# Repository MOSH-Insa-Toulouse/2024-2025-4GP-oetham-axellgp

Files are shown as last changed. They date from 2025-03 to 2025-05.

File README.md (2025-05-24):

# 2024-2025-4GP-oetham-axellgp

## Contexte

Projet réalisé dans le cadre du cours "du capteur au banc de test", lors du deuxième semestre de l'année 2024-2025 de la formation 4ème année Génie Physique. Notre point de référence est l'article _"Pencil Drawn Strain Gauges and Chemiresistors on Paper"_ (Cheng-Wei Lin, Zhibo Zhao, Jaemyung Kim & Jiaxing Huang). Notre capteur est composé d'un simple bout de papier avec du graphite déposé dessus par un crayon à papier. Avec une simple déformation du papier, nous pouvons mesurer la déformation des particules. Le système granulaire du papier subit une modification de résistance et de conductance. Ainsi, nous pourrons utiliser ce capteur comme une jauge de contrainte traditionnelle.

L'objectif de ce projet est de pouvoir réaliser, étape par étape, un dispositif qui nous permettra de mesurer une déformation d'un capteur low-tech.

## Sommaire

- [Contexte](#contexte)
- [Sommaire](#sommaire)
- [Livrables](#livrables)
- [Matériel nécessaire](#matériel-nécessaire)
- [Simulation sur LTSpice](#simulation-sur-ltspice)
- [Design du PCB](#design-du-pcb)
- [Réalisation du Shield](#réalisation-du-shield)
- [Code Arduino](#code-arduino)
- [Application MIT](#application-mit)
- [Datasheet](#datasheet)
- [Conclusion](#conclusion)
- [Contact](#contact)

## Livrables

- Un shield PCB permettant à se relier à une carte Arduino UNO. Ce shield aura à disposition plusieurs composants : un capteur de graphite, un module bluetooth, un ecran OLED, un encodeur rotatoire et un amplificateur transimpédance avec un potentiometre digital.
- Un code Arduino qui pilotera les différents composants.
- Une application Android réalisée sous MIT App Inventor.
- Une datasheet du capteur de graphite avec les données venant d'un banc de test mis en place par les étudiants.

## Matériel nécessaire

Pour produire notre shield, nous avons besoin du matériel suivant :

- Des résistances
- Des capacités
- Un Arduino UNO
- Un amplificateur opérationnel (LTC1050)
- Un potentiomètre digital (MCP41050)
- Un écran OLED
- Un encodeur rotatoire
- Un module bluetooth (HC-05)
- Un servo moteur
- Un flex sensor

## Simulation sur LTSpice

La résistance interne de notre capteur de graphite est de l'ordre du $\text{G}\Omega$. Le courant généré lorsque nous appliquons une tension de 5V est très faible. Pour pouvoir utiliser ce signal, nous le faisons passer par un amplificateur transimpédance. Ce montage est constitué d'un amplificateur opérationnel (AO) pour fournir un signal suffisamment large au convertisseur analogique-numérique (ADC) de l'Arduino UNO.

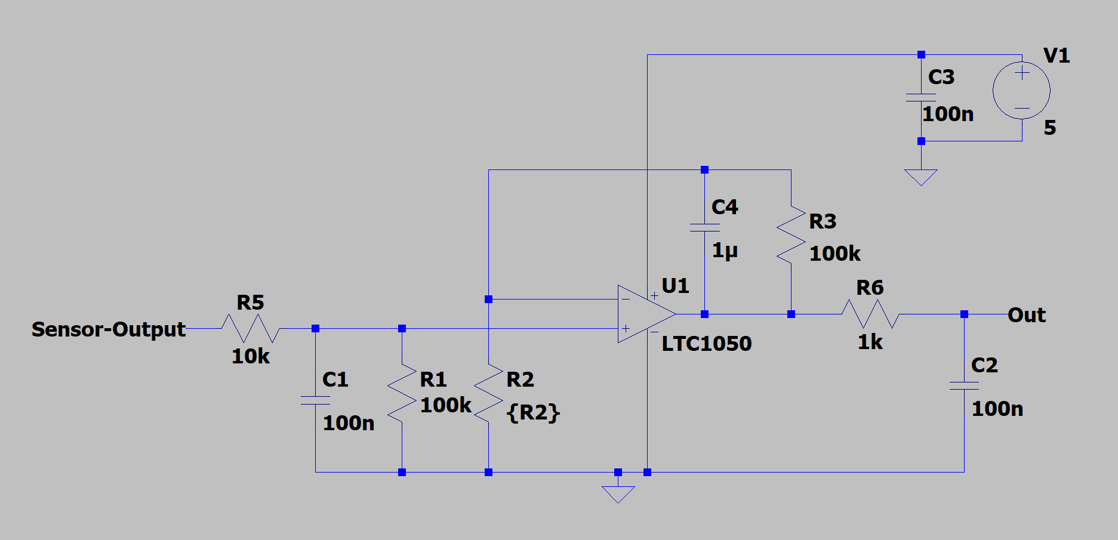
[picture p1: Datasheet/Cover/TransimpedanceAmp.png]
ltspice-circuit


Nous avons choisi un AO de type LTC1050, car il possède une capacité à accepter en entrée un courant très faible et un offset de tension bas. Nous avons besoin d'un offset faible pour ne pas fausser les valeurs de tension envoyées à l'ADC que nous aurons besoin pour la suite.

Dans notre amplificateur, nous avons trois types de filtres différents :

- À l'entrée, un filtre passe-bas passif (composants : $R_1, C_1$) avec une fréquence de coupure de 16Hz. Cela permet de filtrer les bruits du courant en entrée.
- Un autre filtre passe-bas actif de fréquence de coupure de 1.6Hz (composants : $R_3, C_4$) couplé à l'AO. Ce filtre permet d'enlever la composante du bruit à 50Hz du réseau.
- En sortie, un dernier filtre (composants : $R_6, C_2$) de 1.6kHz qui permet de retirer le bruit créé pendant le traitement i.e. bruits des alimentations, de l'horloge...

La résistance $R_5$ est placé en amont de l'AO pour le protéger contre des décharges électrostatiques. Pour notre simulation, nous avons placé la capacité $C_3$ de sorte à ce qu'elle filtre le bruit de l'alimentation. Ainsi, la résistance $R_2$ sera remplacé par une résistance variable (un potentiomètre digital) qui va nous permettre de régler le gain de notre AO en fonction de notre besoin.

Une photo pour montrer que notre montage permet à amplifier notre signal du capteur :

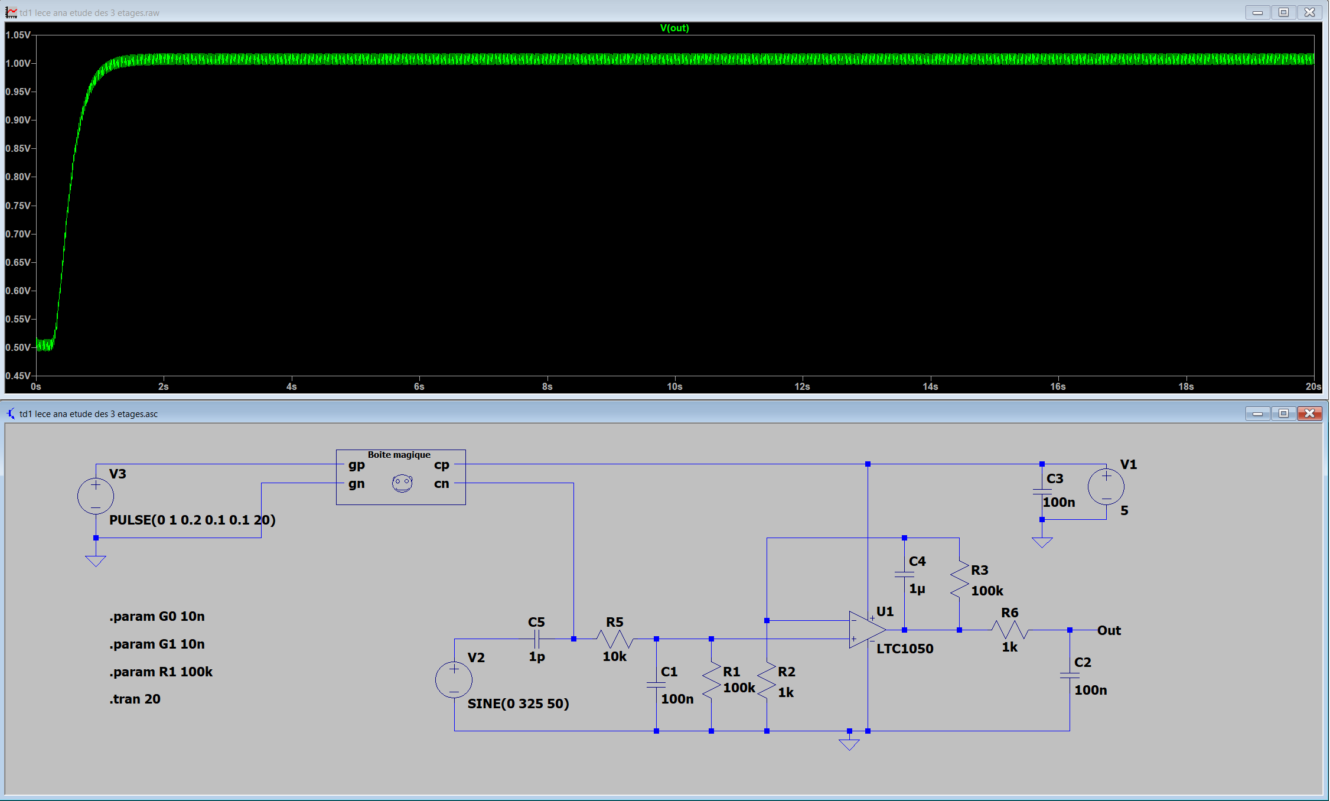
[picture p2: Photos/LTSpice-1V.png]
ltspice-amp


Le signal de sortie est amplifié à 1V, ce qui sera assez pour que notre Arduino puisse le mesurer.

Ensuite, la réponse lorsque nous simulons un courant alternatif pour vérifier que le bruit est bien filtré :

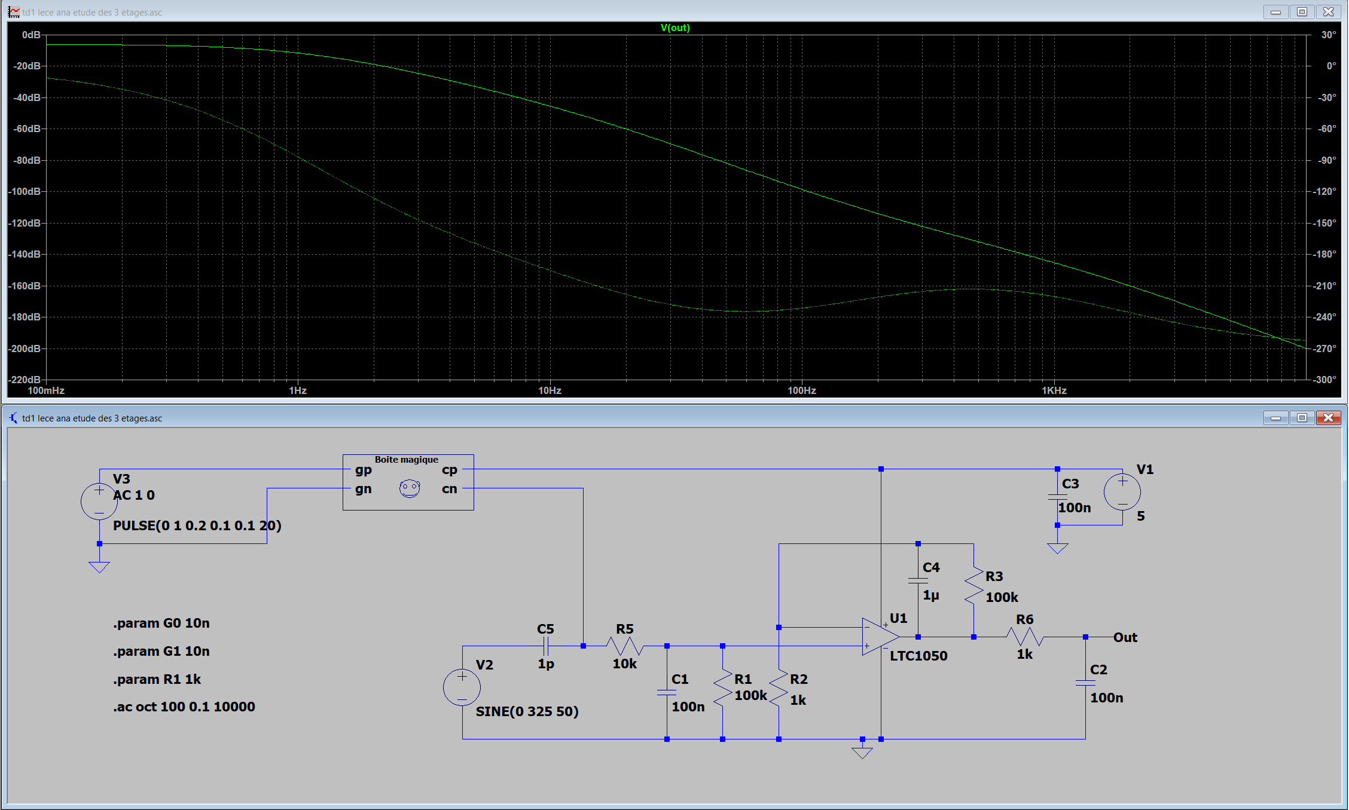
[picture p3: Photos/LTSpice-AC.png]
ltspice-ac


Le bruit du réseau est atténué d'environ 72dB.

La simulation se trouve dans [ce dossier](/LTSpice/).

## Design du PCB

Pour réaliser notre printed circuit board (PCB), nous avons utilisé le logiciel KiCAD 9.0. Dans le logiciel, nous disposons de plusieurs outils de design comme la vue schématique des composants et la vue design du PCB.

La résistance $\text{R}_2$ a été remplace par un potentiomètre numérique de manière à faire varier le gain de notre amplificateur opérationnel (LTC1050). Nous avons également rajouté des composants en plus pour mesurer plus précisément notre capteur graphite. Ces composants seront déposés sur un shield d'Arduino UNO construit à partir d'un Gerber KiCAD.

- Un flex sensor
- Un écran OLED
- Un servo moteur
- Un module bluetooth HC-05

Ensuite, nous avons commencé par réaliser les symboles des composants avec leur schéma électrique sur la partie schématique de KiCAD. Le schéma électrique de l'ensemble de notre shield :

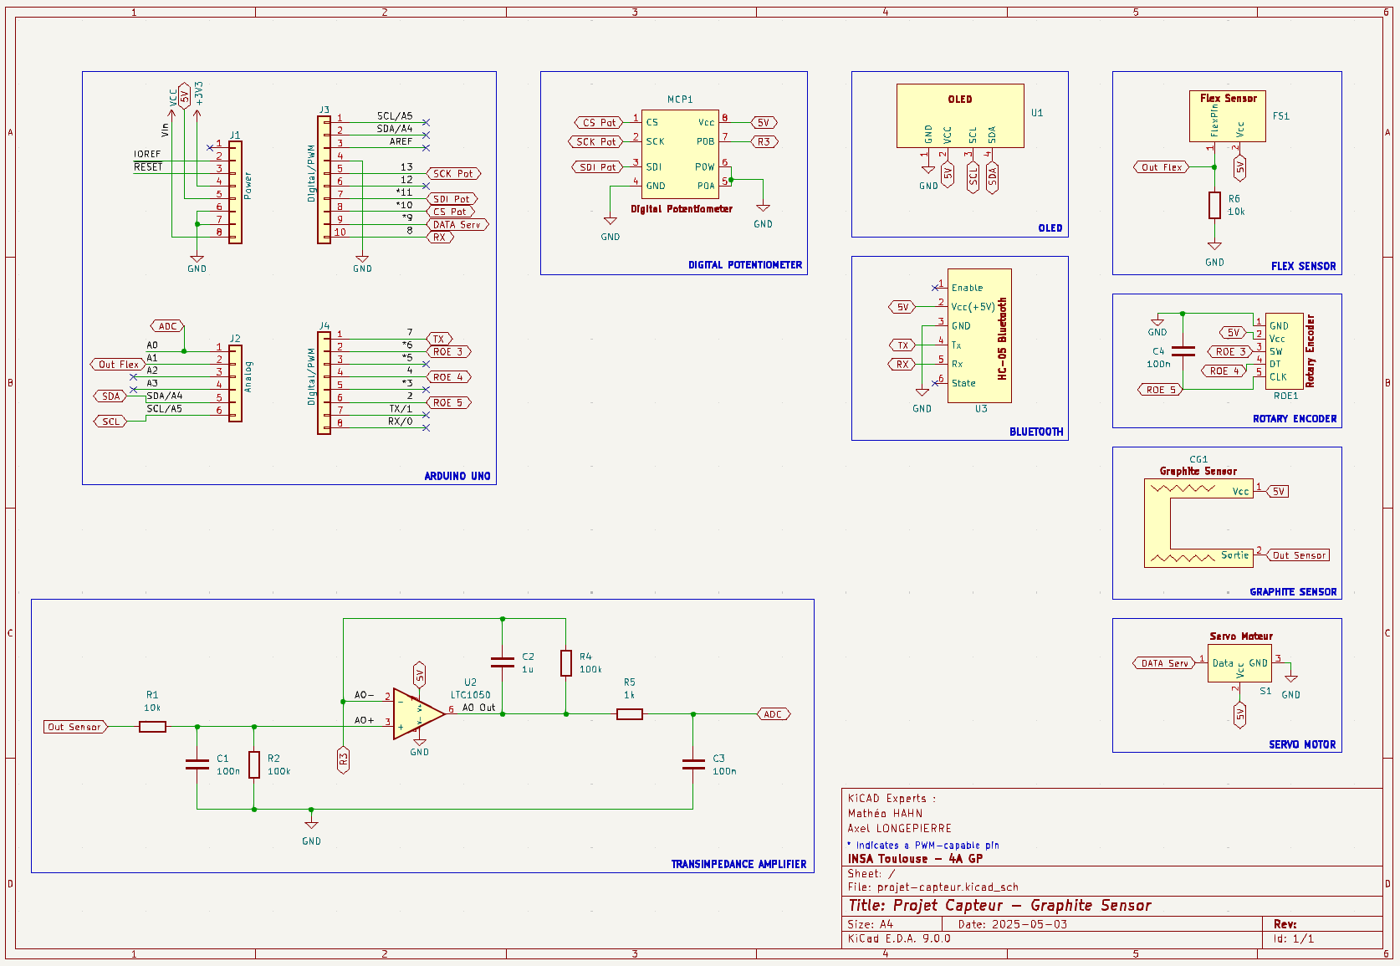
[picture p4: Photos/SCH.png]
design-sch


Par la suite, nous avons créé les empreintes de nos composants puis placées sur notre PCB sur la face PCB de KiCAD. Notre objectif pendant le routage était d'éviter les vias entraînées par le placement des composants. Le PCB créé sur le logiciel :

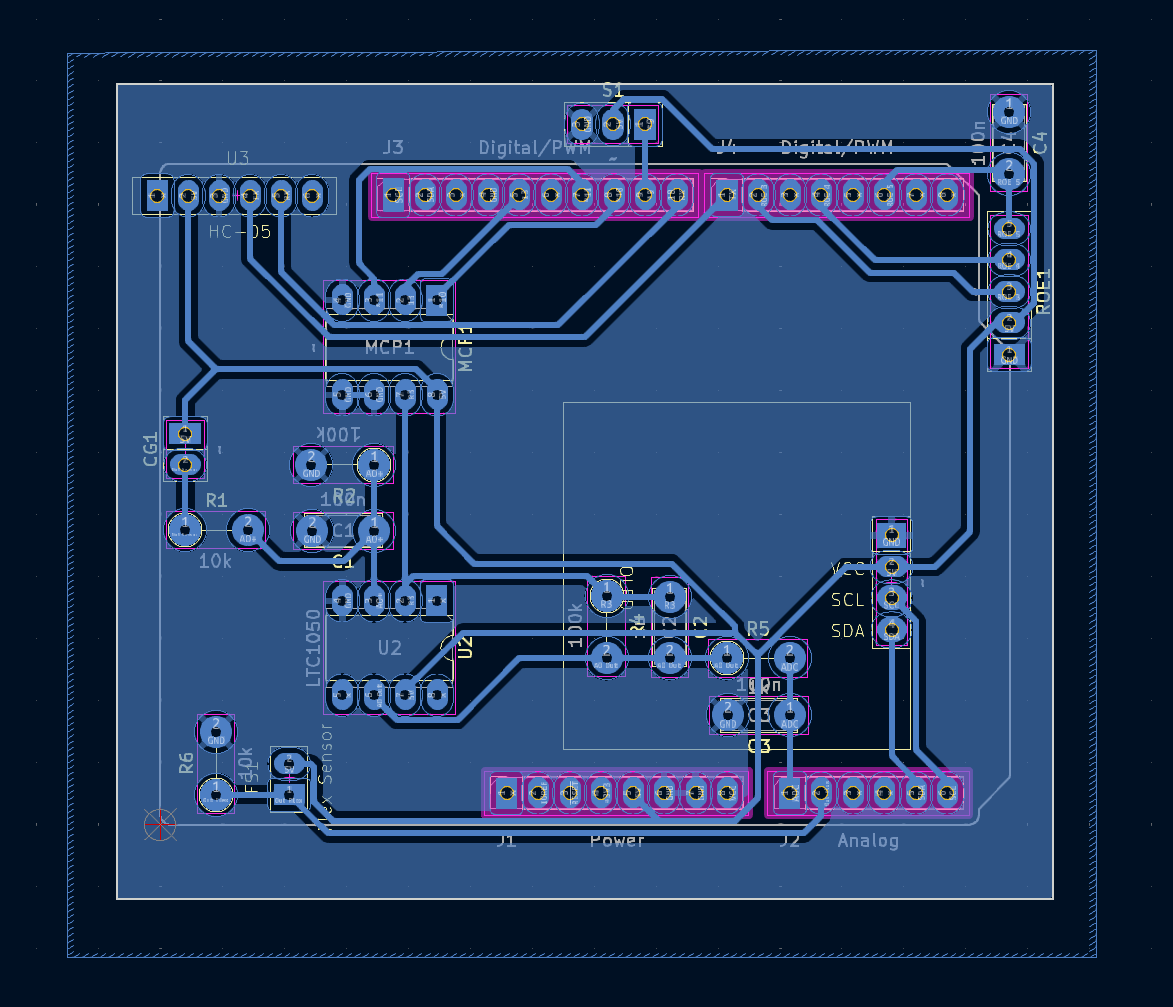
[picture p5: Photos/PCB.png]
design-pcb


La beauté du logiciel est due au fait que nous pouvons générer une vue 3D du shield afin de pouvoir visualiser et vérifier l'emplacement de nos composants. La vue 3D sur KiCAD :

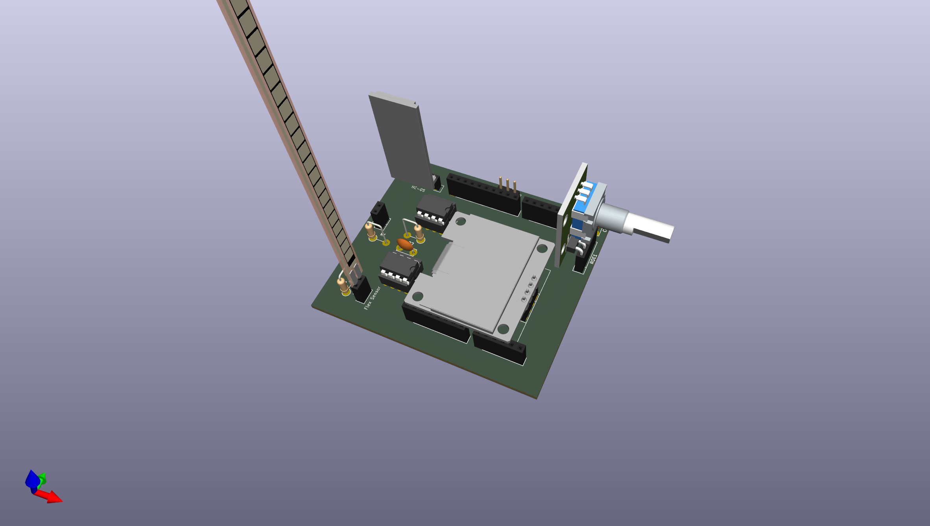
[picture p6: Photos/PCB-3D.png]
pcb-3d


Vous pouvez retrouver toutes les ressources de KiCAD dans notre [dossier KiCAD](/KiCAD/projet-capteur/).

## Réalisation du Shield

Avec l'aide de Catherine Crouzet (aka Cathy pour les 4GP), nous avons fabriqué notre propre PCB. Après avoir envoyé notre fichier Gerber, qui sert comme masque de gravure, Cathy a placé ce masque sur une couche fine de cuivre sur une plaquette d'epoxy. Ensuite, il faut isoler la plaquette, puis l'expose aux UV. Une fois terminer, elle plonge la plaquette dans un bain révélateur afin de retirer la résine non-isolée. Finalement, elle nettoie la plaquette avec de l'acétone pour enlever la résine restante.

Nous avons ensuite effectué au perçage de notre plaquette grâce à une perceuse. On pourra ensuite poser et souder nos composants sur le PCB.

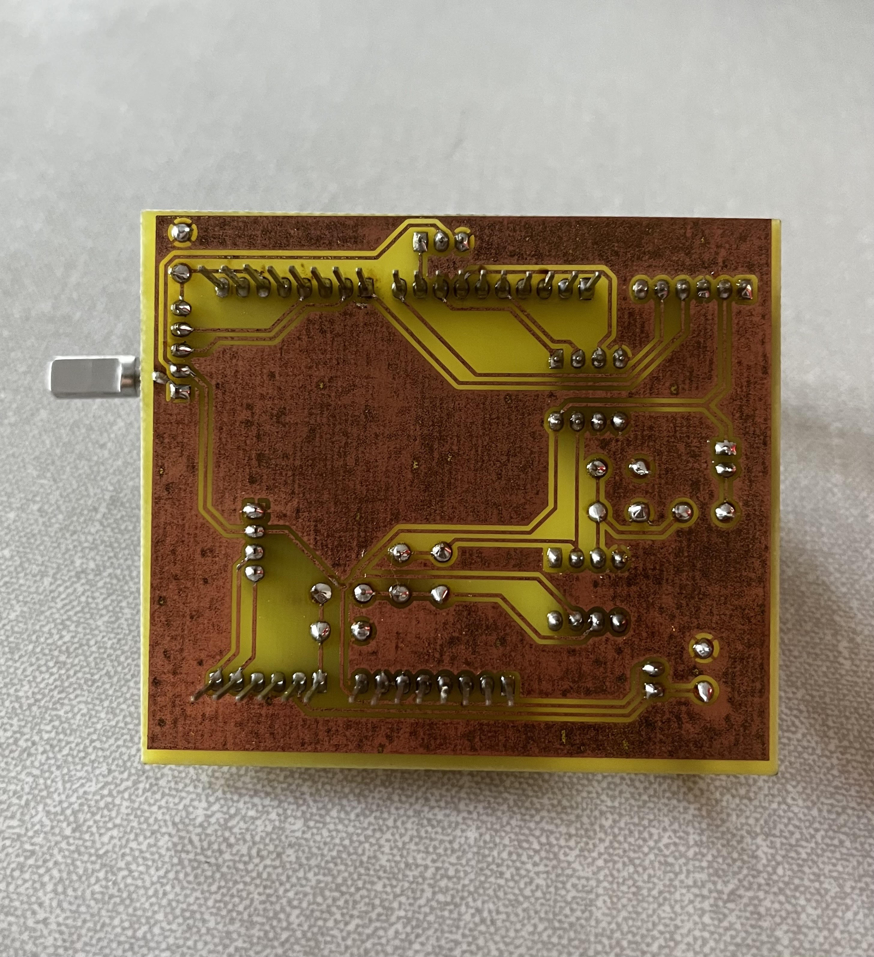
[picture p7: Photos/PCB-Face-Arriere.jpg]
pcb-back


Voici une photo du PCB sur l'Arduino UNO avec tout les composants poser dessus :

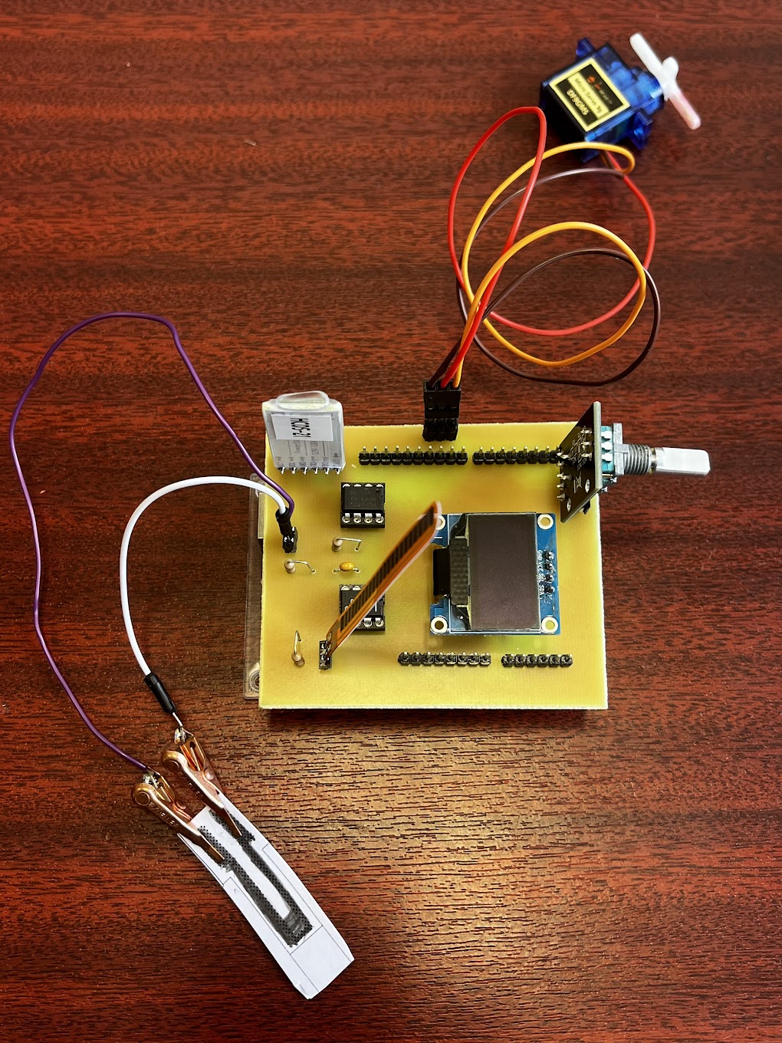
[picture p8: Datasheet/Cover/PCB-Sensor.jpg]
pcb-sensor


## Code Arduino

Le code Arduino a été développé sur l'IDE Arduino 2.3.5. Nous avons utilisé les librairies Adafruit_SSD1306 pour piloter l'écran OLED et SoftwareSerial pour le HC-05. L'écran OLED utilise beaucoup de RAM. Pour contourner ce problème, nous avons utilisé la fonction ```F("Enter String")``` qui envoie les données sur la mémoire flash.

Au lancement du programme, qui est situé [ici](/Arduino/Test-Sensor/), une première calibration est faite à 3V sur le potentiomètre digital pour ne pas saturer la sortie sur l'ADC de l'Arduino. Cette calibration peut être refaite avec un simple appel sur l'application. Nous avons composé un menu avec trois choix :

- Menu 1 : Graphite Sensor
- Menu 2 : Flex Sensor
- Menu 3 : Servo Motor

Le choix du menu se fait avec l'encodeur rotatoire en le tournant pour sélectionner son menu désiré puis ensuite appuyer dessus pour valider la sélection.

Chaque choix du menu appelle une fonction différente qui réalise sa mesure. L'acquisition des données se fait toutes les 200ms. Pour chaque donnée, il faut convertir ce qu'on reçoit par la résolution de l'Arduino qui est de 1024 bytes. Le calcul de la résistance du capteur graphite se fait avec la formule suivante : $R_{es} = R_2 * (1 + \frac{R_4}{R_3}) * \frac{V_{CC}}{V_{graph}} - R_2 - R_1$. L'appellation des résistances est en accord avec notre schématique KiCAD.

## Application MIT

L'application Android a été développé sous MIT App Inventor. Elle reçoit les donnes de notre Capteur Graphite et de Flexion et nous pouvons aussi lui envoyer une position pour le Servo Moteur.

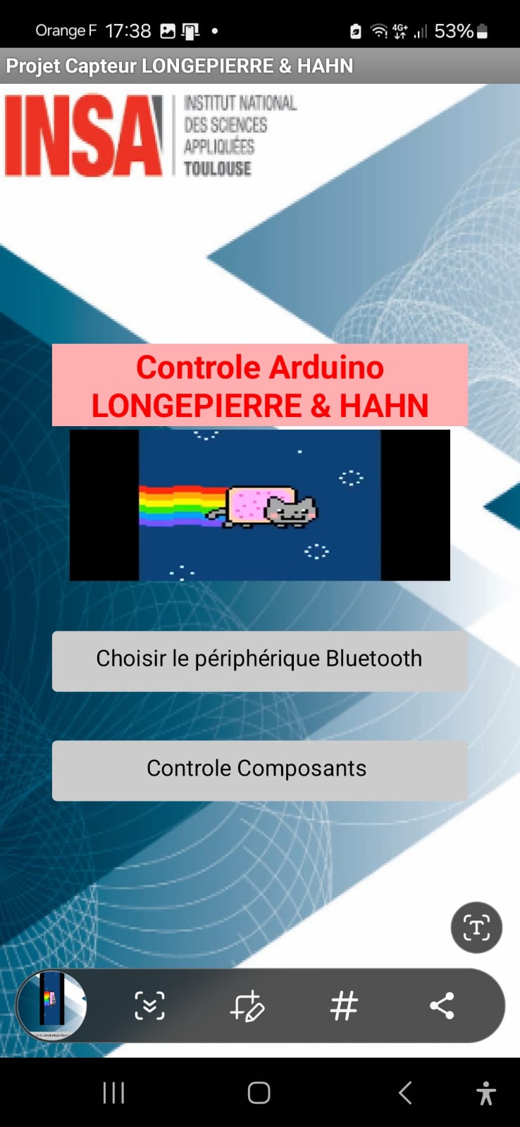
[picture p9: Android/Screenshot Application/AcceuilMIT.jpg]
home-mit


La face-avant de l'application nous donne la possibilité de rentrée dans plusieurs menus :

- Capteur Graphite
- Capteur Flexion
- Servo Moteur

Une fonctionnalité du menu Capteur Graphite est que nous pouvions calibrer directement le capteur depuis l'application s'il y a eu des changements de configuration.

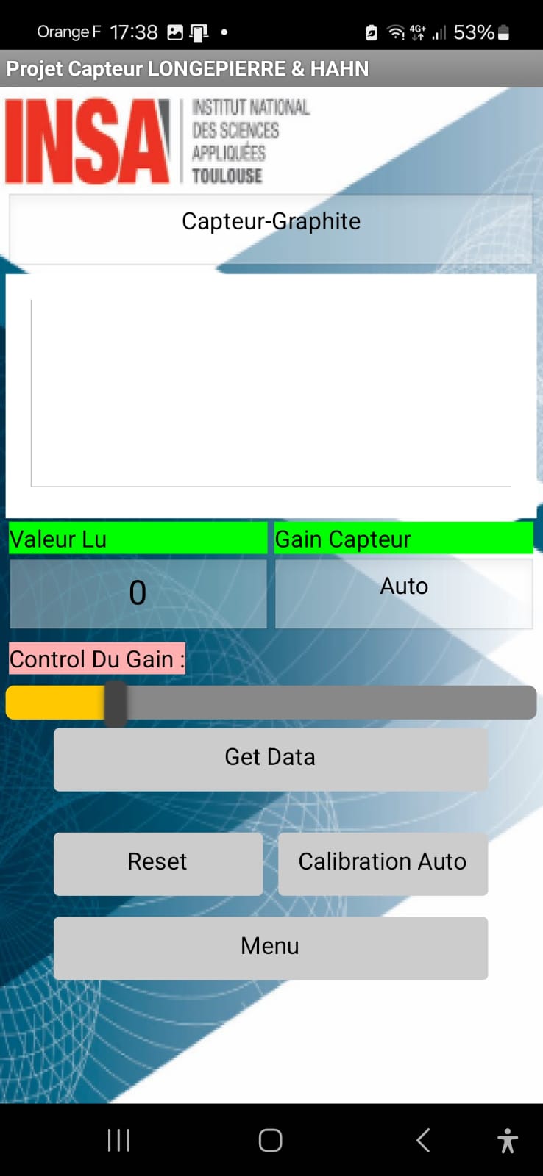
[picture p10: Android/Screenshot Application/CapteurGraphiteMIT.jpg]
graphite-mit


Le menu Capteur Flexion propose un graphique où nous voyons la variation de la résistance du capteur.

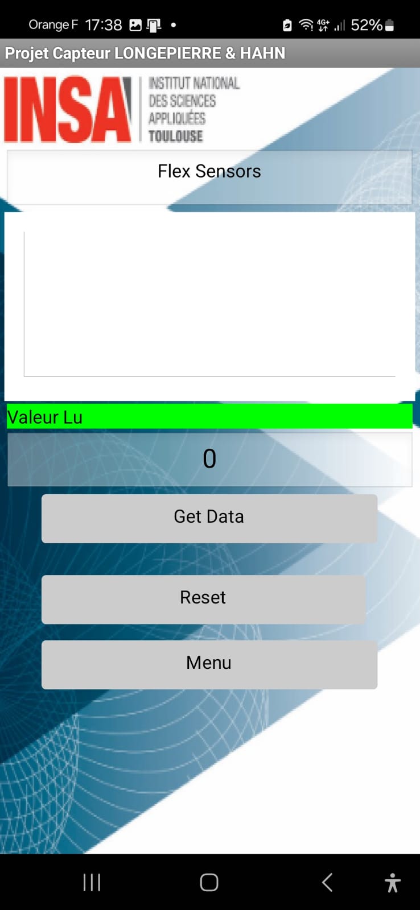
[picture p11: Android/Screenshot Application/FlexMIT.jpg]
flex-mit


Le menu Servo Moteur propose une roue tactile que nous pouvons régler afin d'envoyer la position désirer du Servo Moteur.

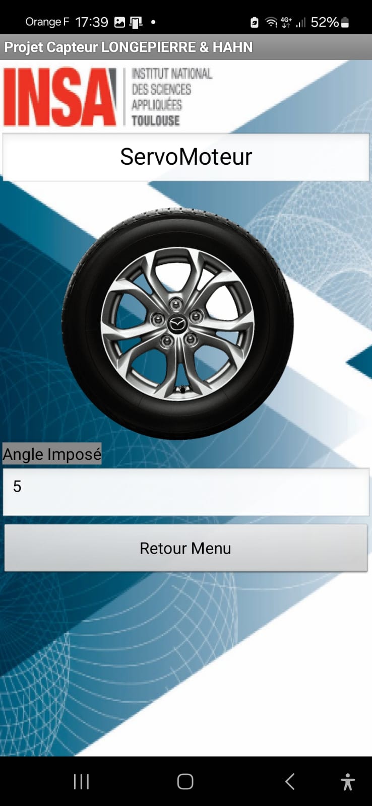
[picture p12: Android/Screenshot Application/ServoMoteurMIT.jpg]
servo-mit


Vous pouvez vous rendre dans [ce dossier](/Android/) pour installer l'application MIT App Inventor ainsi voir les blocks de code qui contrôlent l'application.

## Datasheet

Pour effectuer des mesures, nous avons utilisé une impression 3D de demi-cercles avec des rayons différents.

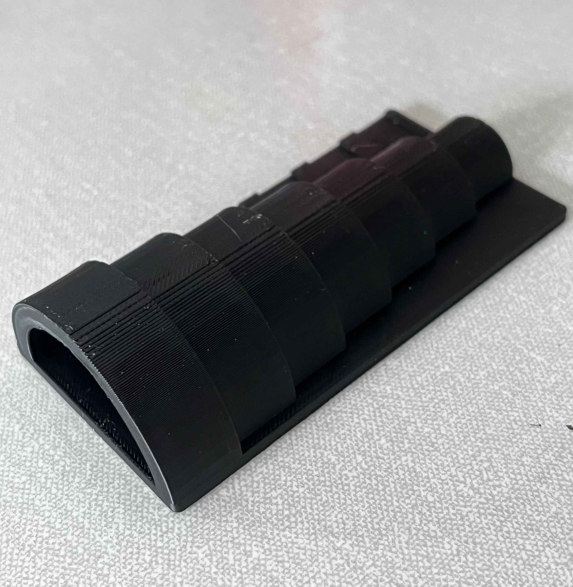
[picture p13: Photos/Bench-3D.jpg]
bench-3D


Les diamètres des demi-cercles vont de 2cm jusqu'à 5cm avec un pas de 0.5cm. Avec la déformation $\epsilon = \frac{e}{D}$ et la résistance électrique $\frac{\Delta R}{R_0}$, nous pouvons tracer les courbes caractéristiques pour des crayons de type F, HB, 4B, 5B :

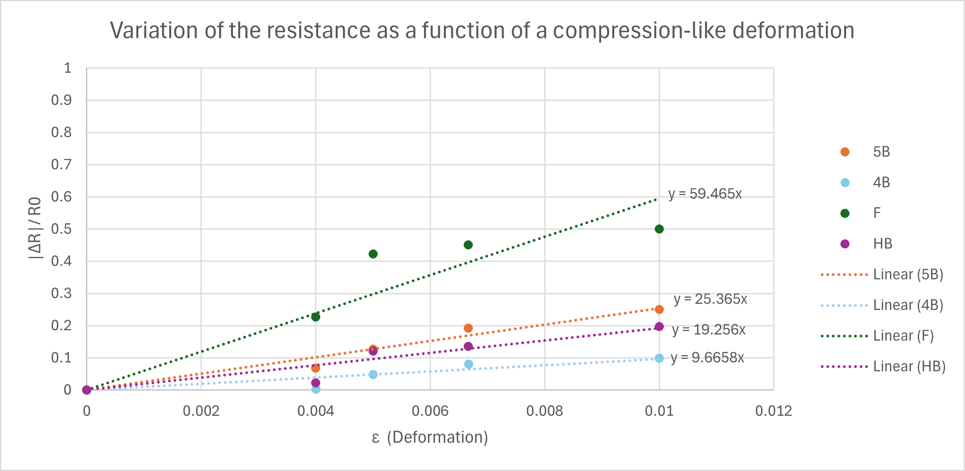
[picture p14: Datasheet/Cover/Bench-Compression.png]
graph-compression


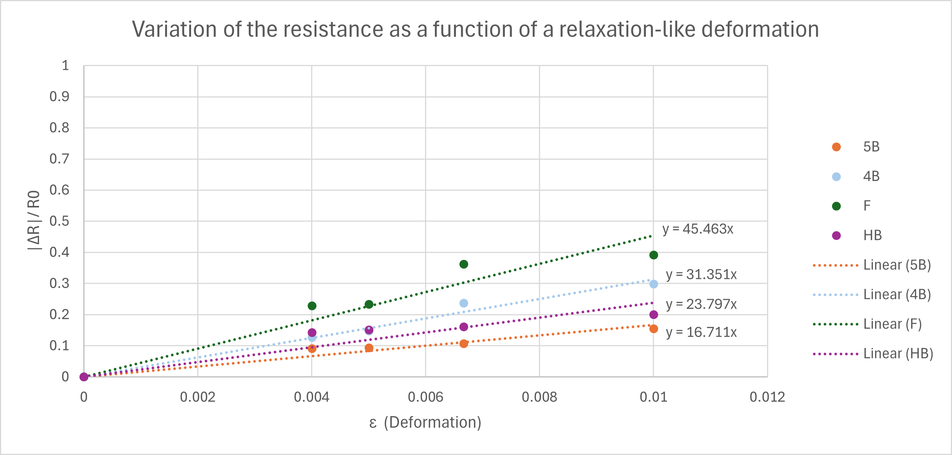
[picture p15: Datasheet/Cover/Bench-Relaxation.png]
graph-relaxation


D'autant plus, nous n'avons aucun moyen pour bien s'assurer que la quantité déposée sur le capteur est la même. Ainsi, à chaque mesure, il y a un nouveau paramètre qui n'est pas le même i.e. on n'écrit pas de la même manière, on applique une force différente pour écrire, on n'applique pas le même angle de déformation. Ces derniers induisent une grosse variation dans la résistance mesurée.

Il se trouve que le flex sensor commercial est bien plus sensible à la déformation d'autant plus il peut être réutiliser beaucoup plus de fois que notre capteur en papier. Notre capteur a chaque utilisation perd de la précision qui impacte notre mesure de résistance. Par contre, notre capteur peut mesurer des résistances dans les $M\Omega$ comparer au flex sensor qui lui peut seulement mesurer des $k\Omega$.

La datasheet se trouve [ici](/Datasheet/).

## Conclusion

Notre capteur a un super potentiel en tant que capteur industriel. Il faudrait à tout prix trouver une méthode pour homogénéiser le dépôt du graphite. Le capteur est peu cher et sensible à des variations en tension ou compression. Nous conseillons de trouver une méthode pour bien appliquer la même force, le même dépôt de graphite et aussi trouver un papier plus adapté à la déformation. Ceci permettra de réaliser un capteur plus performant avec un potentiel plus élevé pour être industrialisable.

Pour le moment, notre capteur en papier est un super outil pour pouvoir comprendre et conceptionner notre propre PCB et ainsi un banc de test afin de mesurer des quantités physiques qui peuvent nous intéresser. Effectivement, le capteur présente beaucoup de lacunes de précisions et le matériel à disposition ne fonctionne pas parfaitement. Ce capteur est l'outil pédagogique ultime et nous permet d'apprendre et de peaufiner des nouvelles connaissances.

## Contact

Pour toutes questions, vous pouvez nous contacter aux adresses suivantes :

- Mathéo HAHN : <hahn@insa-toulouse.fr>
- Axel LONGEPIERRE : <longepierre@insa-toulouse.fr>

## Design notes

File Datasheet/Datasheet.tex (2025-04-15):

%% Example data sheet
%% Feel free to modify and use this file for any purpose, under
%% either the LaTeX Project Public License or under public domain.

% Options here are passed to the article class.
% Most common options: 10pt, 11pt, 12pt
\documentclass[10pt]{datasheet}

% Input encoding and typographical rules for English language
\usepackage[utf8]{inputenc}
\usepackage[english]{babel}
\usepackage[english]{isodate}

% tikz is used to draw images in this example, but you can
% also use \includegraphics{}.
\usepackage{tikz}
\usepackage{pgfplots}
\usepackage{circuitikz}
\usetikzlibrary{calc}

% These define global texts that are used in headers and titles.
\title{Low-Tech Graphite Sensor}
\author{M.HAHN et A.LONGEPIERRE}
\date{April 2025}
\revision{Revision 1}
\course{MOSH}
\companylogo{\hfill}

\begin{document}

\maketitle

\begin{tikzpicture}[remember picture, overlay, shift={(current page.south west)}]
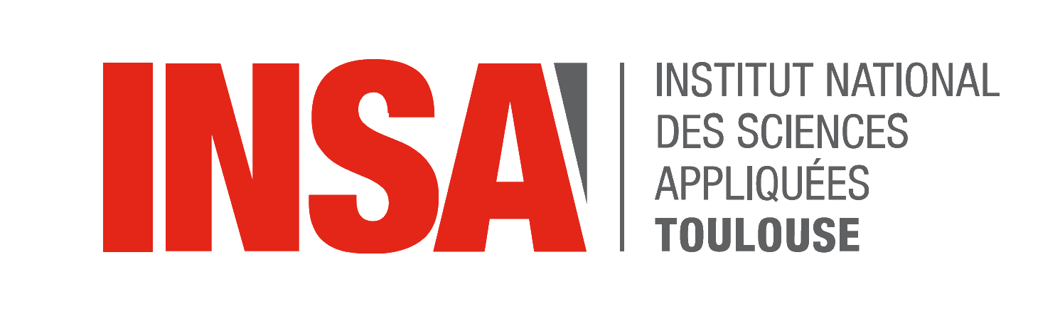
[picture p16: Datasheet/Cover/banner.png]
    \node[anchor=north west] at (1.3,27) {};
\end{tikzpicture}

\section{Features}

\begin{itemize}
\item{Low power usage (3.3V-5V)}
\item{Low cost and low tech}
\item{Plug-n-play}
\item{Ergonomic and easily repairable}
\end{itemize}

\section{Applications}

\begin{itemize}
\item{Test findings of \it{Pencil Drawn Strain Gauges and Chemiresistors on Paper}\footnotemark{}}
\item{Applied using a transimpedance amplifier connected to the ADC of an Arduino card}
\item{Pedagogical tool for students to design and implement their own PCB design}
\end{itemize}

\section{General Description}
This innovative sensor, conceptualized and made by students from the Applied Physics Department of INSA Toulouse, is a tool inspired by the publication 
\textit{Pencil Drawn Strain Gauges and Chemiresistors on Paper}\footnotemark[\value{footnote}]. This research paper provides a simple, cost-efficient, and highly pedagogical tool for students 
to master their skills in Physics, Electronics, and Sensor Design. The sensor presented in the publication is a simple piece of paper with a layer of graphite 
on top of it, deposited with a pencil. 

Due to the deposited graphite on the piece of paper, the electrons are able to move freely from particle to particle due to quantum tunnelling. This effect is
extremely sensitive to the slightest movement of the paper. We observe that compressing or stretching the graphite will change the resistivity of the 
sensor. 

\footnotetext{LIN, Cheng-Wei, ZHAO, Zhibo, KIM, Jaemyung et HUANG, Jiaxing, 2014. Pencil Drawn Strain Gauges and Chemiresistors on Paper. Scientific Reports. 22 janvier 2014. Vol.4, n°1, pp.3812. DOI 10.1038/srep03812.}

% Switch to next column
\vfill\break

\hspace{1pt}

\vspace{0.65cm}

\begin{figure}[h!]
	\centering
	
	\caption{\small{Graphite Sensor connected to the PCB}}
\end{figure}

\vspace{1.5cm}

\begin{figure}[h!]
	\centering
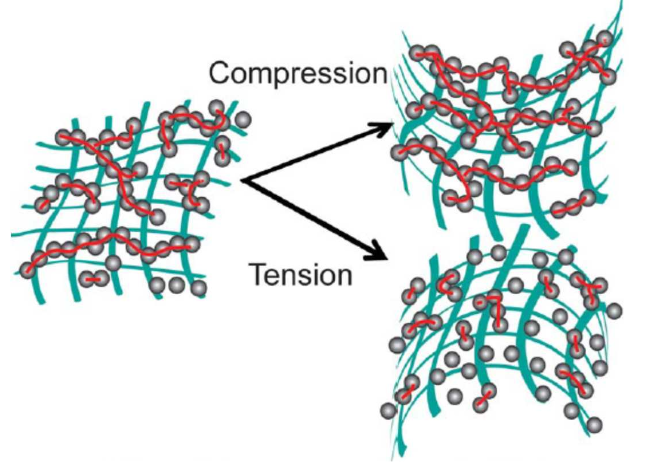
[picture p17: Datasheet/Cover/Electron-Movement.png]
	
	\caption{\small{Compression and tension in a granular system}}
\end{figure}

% For wide tables, a single column layout is better. It can be switched
% page-by-page.
\onecolumn

\section{Electrical Diagram}

\begin{figure}[h!]
    \begin{minipage}[ts]{.47\linewidth}
        \centering
        \captionsetup{justification=centering}
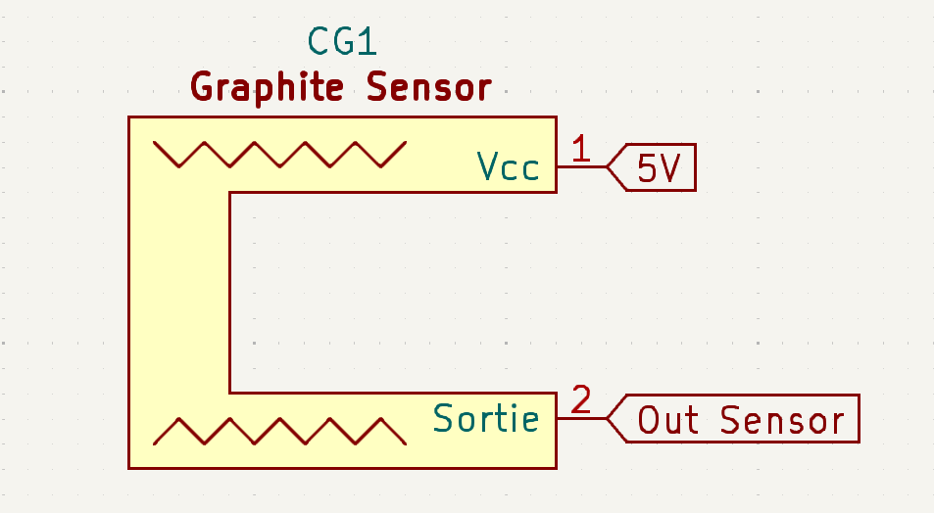
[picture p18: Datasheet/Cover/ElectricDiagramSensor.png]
        
        \caption{\small{Schematic of the Graphite Sensor}}
    \end{minipage}
    \begin{minipage}[b]{.45\linewidth}
        \centering
        \caption*{Table 1: Specifications of the Electrical Diagram}
            \begin{tabularx}{\textwidth}{l | c | X}
                \thickhline
                \textbf{Parameter} & \textbf{Pin} & \textbf{Symbol} \\
                \hline
                Supply Voltage & 1 & V$_{\text{CC}}$ \\ 
                \hline
                Out Sensor & 2 & V$_{\text{out}}$ \\
                \thickhline
            \end{tabularx}
    \end{minipage}
\end{figure}

\textbf{Note:} Both pins are invertible.

\setcounter{table}{1}

\section{Electrical Specifications}

\begin{table}[h]
\begin{threeparttable}
\caption{Values of the resistance of each type of pencil}
\begin{tabularx}{\textwidth}{l | c | c | c | X}
    \thickhline
    \textbf{Pencil Type} & \textbf{Min.} & \textbf{Typ.} & \textbf{Max.} &
    \textbf{Unit} \\
    \hline
    F  & 2.1 & 2.5 & 5 & $\text{M}\Omega$ \\    % & \multirow{4}{*}{Values highly depend on the amount of graphite deposited} \\
    HB & 1.9 & 2.7 & 3.8 & $\text{M}\Omega$ \\  % &  \\
    4B & 0.9 & 1.1 & 1.5 & $\text{M}\Omega$ \\  % &  \\
    5B & 0.8 & 0.9 & 1.3 & $\text{M}\Omega$ \\  % &  \\
    \thickhline
\end{tabularx}
\end{threeparttable}
\end{table}

\textbf{Note:} Values highly depend on the amount of graphite deposited ($\pm$ 5\%). 

\section{Absolute Maximum Ratings}

\begin{table}[h!]
\begin{threeparttable}
\caption{Absolute Maximum Ratings of the Graphite Sensor}
\begin{tabularx}{\textwidth}{l | c | c c c | X}
    \thickhline
    \textbf{Parameter} & \textbf{Symbol} & \textbf{Min.} & \textbf{Typ.} & \textbf{Max.} & \textbf{Unit} \\
    \hline
    Supply Voltage & V$_{\text{CC}}$ & - & 5.0 & - & V \\
    \hline
    Temperature & T & 10.0 & - & 30.0 & $^\circ$C \\
    Humitidy & - & 30 & - & 60 & \% \\
    \hline
    Paper Thickness & - & 0.15 & - & 0.30 & mm \\
    Pencil Tone\tnote{1} & - & 4B & - & 2H & - \\
    \thickhline
\end{tabularx}
\begin{tablenotes}
\item[1]{Corresponds to the US grading system.}
\end{tablenotes}
\end{threeparttable}
\end{table}

\newpage

\section{Performance Characteristics}

\begin{figure}[h!]
	\centering
	
    \captionsetup{justification=centering}
	\caption{\small{Characteristics of a compression-like deformation}}
\end{figure}

\begin{figure}[h!]
	\centering
	
    \captionsetup{justification=centering}
	\caption{\small{Characteristics of a relaxation-like deformation}}
\end{figure}

\newpage

\section{Applications}

\begin{figure}[h!]
	\centering
	
    \captionsetup{justification=centering}
	\caption{\small{The transimpedance amplifier found on our board}}
\end{figure}

The sensor is connected to a transimpedance amplifier circuit. The circuit is equipped with a 
low-pass and high-pass filters to cancel out the noise due to the 50Hz from the sector and the amplification 
of the signal. 

The output signal of the amplifier, in our application, is transmitted to the Analog-to-digital (ADC) converter on the Arduino Uno
card. We have to make sure that the signal the ADC receives does not saturate it, thus the need for this type of amplifier. 

On our PCB, we have installed a digital potentiometer in lieu of the $\text{R}_2$ resistance in order to match the amplification of the circuit
for each pencil tone. We can calculate the value of this resistance, knowing the value of the final voltage, with the following formula :

\begin{equation*}
    R_{dp} = \frac{V_{CC}}{V_{ADC}}\times R_1\Big(1 + \frac{R_3}{R_2}\Big) - R_1 - R_5
\end{equation*}

\end{document}

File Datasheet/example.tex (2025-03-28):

%% Example data sheet
%% Feel free to modify and use this file for any purpose, under
%% either the LaTeX Project Public License or under public domain.

% Options here are passed to the article class.
% Most common options: 10pt, 11pt, 12pt
\documentclass[10pt]{datasheet}

% Input encoding and typographical rules for English language
\usepackage[utf8]{inputenc}
\usepackage[english]{babel}
\usepackage[english]{isodate}

% tikz is used to draw images in this example, but you can
% also use \includegraphics{}.
\usepackage{tikz}
\usepackage{pgfplots}
\usepackage{circuitikz}
\usetikzlibrary{calc}

% These define global texts that are used in headers and titles.
\title{Low-Tech Graphite Sensor}
\author{Mathéo HAHN et Axel LONGEPIERRE}
\date{March 2025}
\revision{Revision 1}
\companylogo{\hfill}

\begin{document}

\maketitle

\begin{tikzpicture}[remember picture, overlay, shift={(current page.south west)}]
    \node[anchor=north west] at (1.3,27) {};
\end{tikzpicture}

\section{Features}

\begin{itemize}
\item{Low power usage (3.3V-5V)}
\item{Low cost and low tech}
\item{Plug-in-play}
\item{Ergonomic and easily repairable}
\end{itemize}

\section{Applications}

\begin{itemize}
\item{Test findings of \it{Pencil Drawn Strain Gauges and Chemiresistors on Paper}\footnotemark{}}
\item{Pedagogical tool for students to design and implement their own PCB design}
\end{itemize}

\section{General Description}
This innovative sensor conceptionalized and made by students from the Applied Physics Department of INSA Toulouse is a tool inspired by the publication 
\textit{Pencil Drawn Strain Gauges and Chemiresistors on Paper}\footnotemark[\value{footnote}]. This research paper provides a simple, cost-efficient, and highly pedagogical tool for students 
to master their skills in Physics, Electronics, and Sensor Design. The sensor presented in the publication is a simple piece of paper with a layer of graphite 
on top of it, deposited by a pencil. 

Due to the graphite deposited on the piece of paper, the electrons are able to move freely from particle to particle due to quantum tunnelling. This effect is
extremely sensitive to the slightest movement of the piece of paper. We observe that compressing or stretching the graphite will change the resistivity of the 
sensor. 

\footnotetext{LIN, Cheng-Wei, ZHAO, Zhibo, KIM, Jaemyung et HUANG, Jiaxing, 2014. Pencil Drawn Strain Gauges and Chemiresistors on Paper. Scientific Reports. 22 janvier 2014. Vol.4, n°1, pp.3812. DOI 10.1038/srep03812.}

% Switch to next column
\vfill\break

\begin{figure}[h]
    \begin{circuitikz}[european]
        \node[op amp] (amp1) {};
        \node[op amp, below = 0.5cm, xscale = -1] (amp2) {};
        \draw (amp1.out) |- (amp2.-);
        \draw (amp2.-) ++(0, 0.3cm) node[circ]{} to +(2,0) node[above left]{5};
        \draw (amp2.out) to (amp1.+);
        \draw (amp1.+) ++(0, -0.3cm) node[circ]{} to +(-2,0) node[above right]{2};
        \draw (amp1.-) to +(-2,0) node[above right]{1};
        \draw (amp2.+) to +(2,0) node[above left]{4};
        \draw (amp1.out) +(0,0.5cm) node (Vdd) {$\mathrm{V_{DD}}$};
        \draw (Vdd.east) to +(1.5,0) node [above left]{6};
        \draw (amp2.out) +(0,-0.5cm) node (Vss) {$\mathrm{V_{SS}}$};
        \draw (Vss.west) to +(-1.6,0) node [above right]{3};
        \draw ($(amp1.north west) + (-0.5,0.5)$) rectangle ($(amp2.south west) + (0.5,-0.5)$);
    \end{circuitikz}
    \caption{Pinout and internal circuit}
\end{figure}

\begin{figure}[h]
    \begin{tikzpicture}
        \sffamily
        \begin{axis}[
            width=7cm,
            xlabel={Number of LaTeX packages},
            ytick distance=20,
            yticklabel={\pgfmathprintnumber{\tick}\%},
            xmajorgrids, ymajorgrids]
        \addplot[smooth,mark=*] plot coordinates {
            (0,4)
            (5,50)
            (10,80)
            (15,95)
            (20,98)
        };
        \end{axis}
    \end{tikzpicture}
    \caption{Typical data sheet production efficiency}
\end{figure}

% For wide tables, a single column layout is better. It can be switched
% page-by-page.
\onecolumn

\section{Electrical Specifications}
All specifications are in $-40\degree C \leq T_A \leq 85\degree C$ unless otherwise noted.

\begin{table}[h]
\begin{threeparttable}
\caption{Example Data Sheet Specifications}
\begin{tabularx}{\textwidth}{l | c | c c c | c | X}
    \thickhline
    \textbf{Parameter} & \textbf{Symbol} & \textbf{Min.} & \textbf{Typ.} & \textbf{Max.} &
    \textbf{Unit} & \textbf{Conditions} \\
    \hline
    Page width  & $p_w$ & 20.9 & 21.0 & 21.1 & cm & \multirow{2}{*}{Standard A4 paper} \\
    Page height & $p_h$ & 29.6 & 29.7 & 29.8 & cm &  \\
    \hline
    Insulation voltage & $E_{max}$\tnote{1} & & 1 & & kV & \\
    \thickhline
\end{tabularx}
\begin{tablenotes}
\item[1]{Based on characterization data, not tested in production.}
\end{tablenotes}
\end{threeparttable}
\end{table}

\section{Absolute Maximum Ratings}

\begin{table}[h]
\caption{Absolute Maximum Ratings of Example Data Sheet}
\begin{tabularx}{\textwidth}{l | X}
    \thickhline
    \textbf{Parameter} & \textbf{Rating} \hspace{5cm} \\
    \hline
    Daily exposure to LaTeX & 24 hours \\
    \thickhline
\end{tabularx}
\end{table}

\textbf{Note:} Stresses above those listed under Absolute Maximum Ratings can
cause permanent damage to the device. This is a stress rating only. Functional
operation of the device is not implied in any conditions above those indicated
in the Electrical Specifications section.

\end{document}

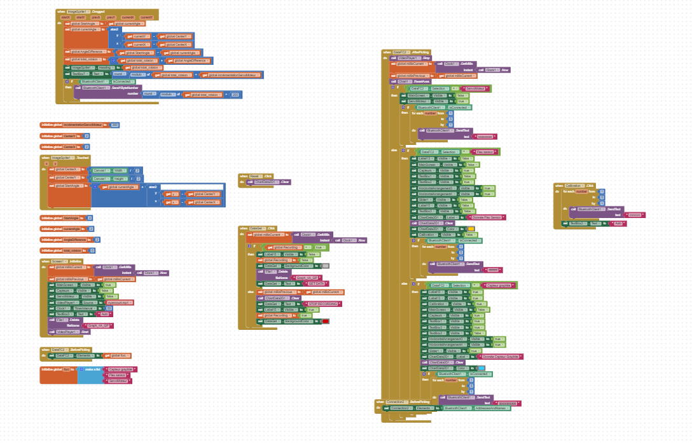
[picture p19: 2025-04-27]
Android/Code MIT App/faceBlockMIT_1.png

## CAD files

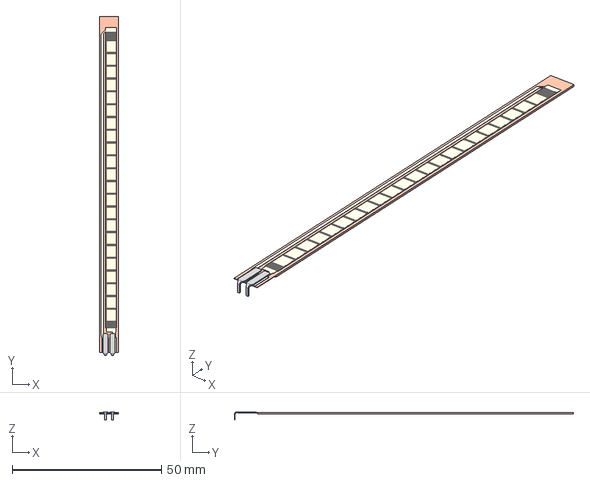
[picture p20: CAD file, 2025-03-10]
KiCAD/projet-capteur/Modeles 3D/FS-L-0095-103-ST - Assembly.stp
6.45 x 113.5 x 2.77 mm
FS-L-0095-103-ST - Base
FS-L-0095-103-ST - Top

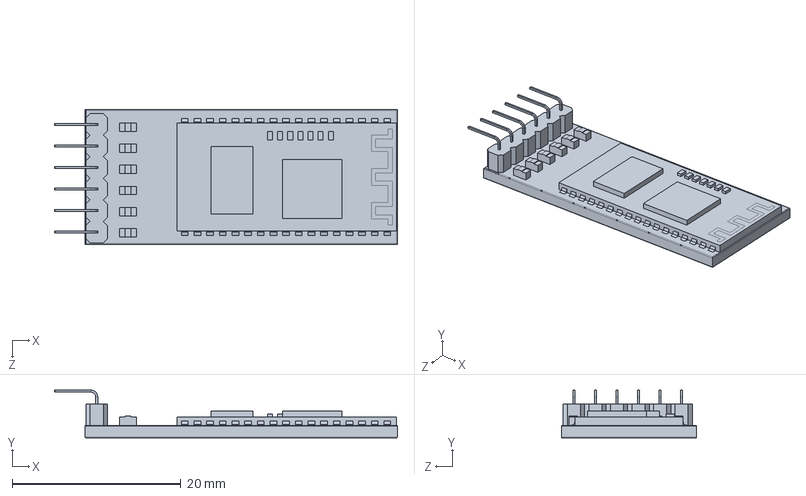
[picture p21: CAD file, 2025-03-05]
KiCAD/projet-capteur/Modeles 3D/HC05.STEP
40.6 x 5.67 x 16.0 mm

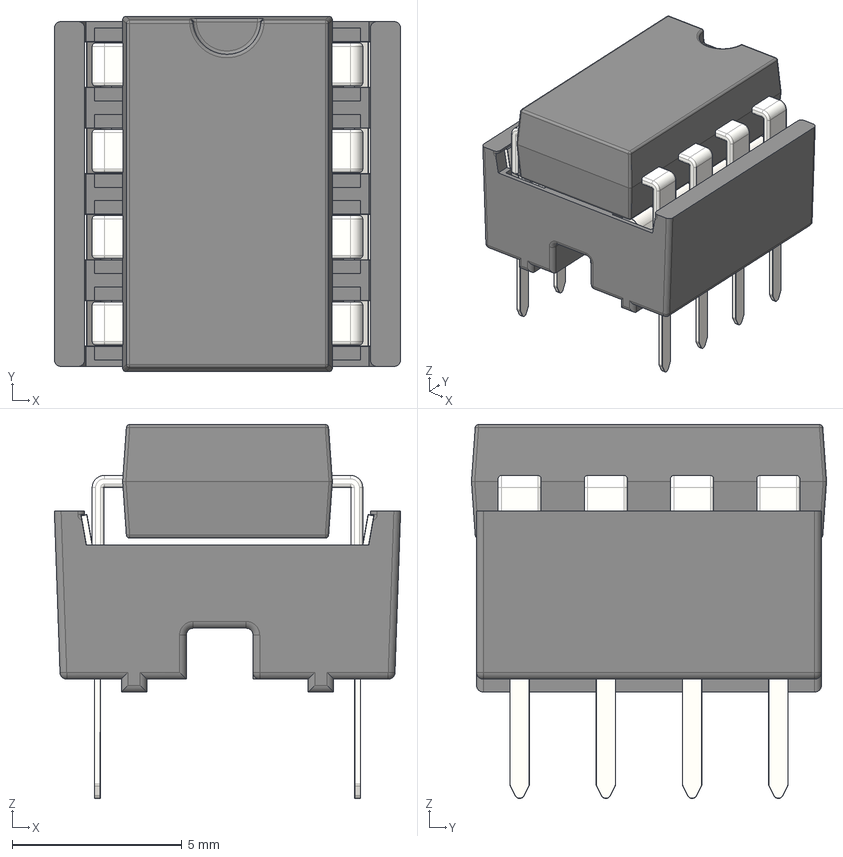
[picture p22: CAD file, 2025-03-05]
KiCAD/projet-capteur/Modeles 3D/DIP-8 W7.62mm IC with Socket.stp
10.2 x 10.5 x 11.0 mm
Stamped Dual Wipe Contact for DIP Sockets x 8
Body DIP-8 P7.62mm Socket
IC Beinchen x 8
DIP-8 W7.62

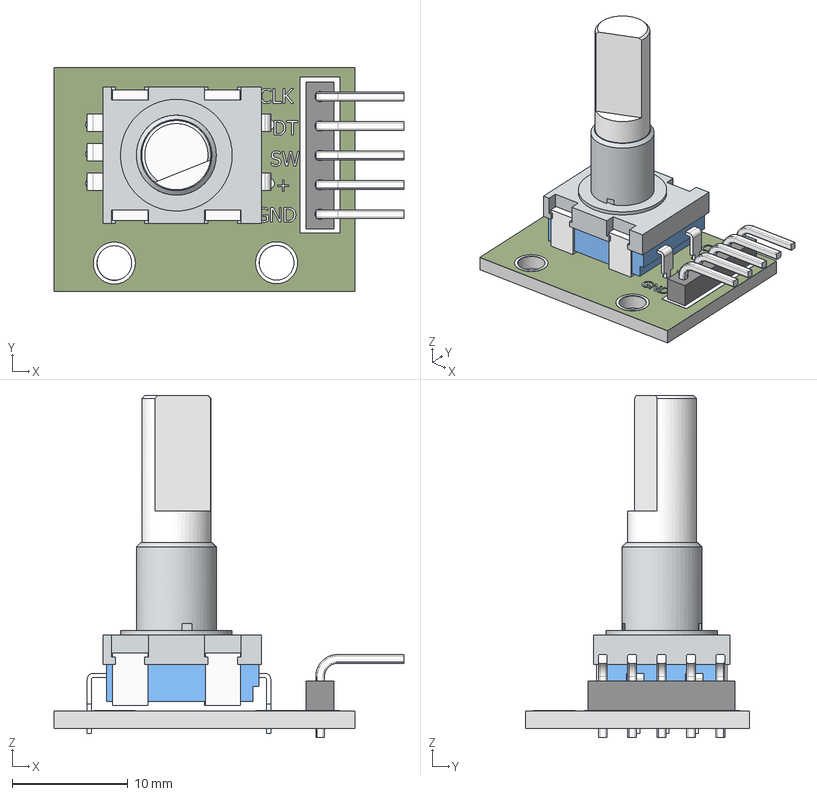
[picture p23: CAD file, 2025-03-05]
KiCAD/projet-capteur/Modeles 3D/rotary+encoder_14mm_hole_spc.stp
30.2 x 19.3 x 29.6 mm
pcb
mtg flange
body_encoder
5 pin header
90d pin_header x 5
decal_encoder
pins_encoder body_2 x 5
shaft_encoder

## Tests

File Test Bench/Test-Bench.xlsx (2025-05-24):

 |  |  | 4B |  |  | 5B |  |  | 6B |  |  | F |  |  | HB
d | ε |  | V0 | V | Diff | V0 | V | Diff | V0 | V | Diff | V0 | V | Diff | V0 | V | Diff | e (paper)
 | 0 | Compression |  |  | 0 |  |  | 0 |  |  | 0 |  |  | 0 |  |  | 0 | 0.02
5 | 0.004 |  | 3.1 | 3.11 | 0.003225806452 | 3.35 | 3.58 | 0.06865671642 | 3.61 | 3.7 | 0.02493074792 | 1.06 | 1.3 | 0.2264150943 | 2.74 | 2.8 | 0.02189781022
4 | 0.005 |  | 3.1 | 3.25 | 0.04838709677 | 3.22 | 3.63 | 0.1273291925 | 3.33 | 3.59 | 0.07807807808 | 0.9 | 1.28 | 0.4222222222 | 2.57 | 2.88 | 0.1206225681
3 | 0.006666666667 |  | 3.1 | 3.35 | 0.08064516129 | 3.22 | 3.84 | 0.1925465839 | 3.3 | 3.51 | 0.06363636364 | 0.93 | 1.35 | 0.4516129032 | 2.43 | 2.76 | 0.1358024691
2 | 0.01 |  | 3.1 | 3.41 | 0.1 | 2.83 | 3.54 | 0.2508833922 | 3.15 | 3.27 | 0.0380952381 | 0.72 | 1.08 | 0.5 | 2.38 | 2.85 | 0.1974789916
 |  |  | Pot pos | 35 |  | Pot pos | 100 |  | Pot pos | 150 |  | Pot pos | 10 |  | Pot pos | 200
 |  |  | 5B Tension |  |  | 4B Tension |  |  | F Tension |  |  | HB Tension
d | ε |  | V0 | V | Diff | V0 | V | Diff | V0 | V | Diff | V0 | V | Diff |  |  |  | e (paper)
 | 0 | Tension |  |  | 0 |  |  | 0 |  |  | 0 |  |  | 0 |  |  |  | 0.02
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

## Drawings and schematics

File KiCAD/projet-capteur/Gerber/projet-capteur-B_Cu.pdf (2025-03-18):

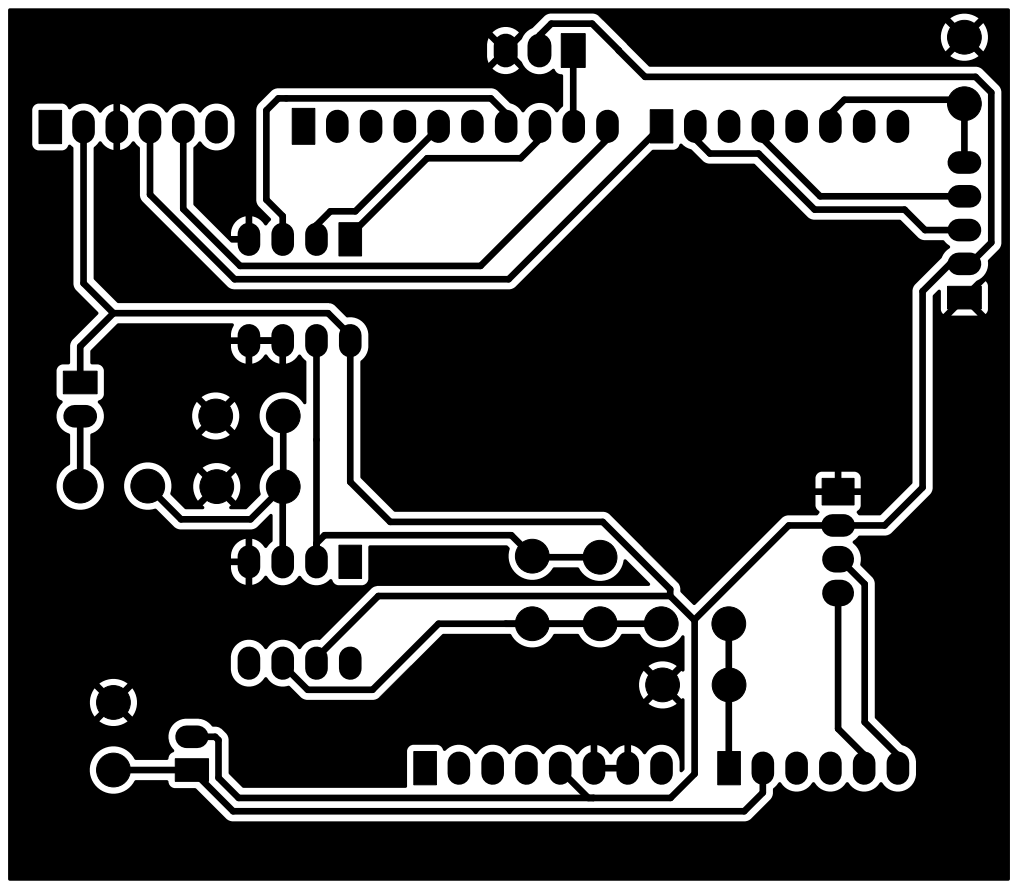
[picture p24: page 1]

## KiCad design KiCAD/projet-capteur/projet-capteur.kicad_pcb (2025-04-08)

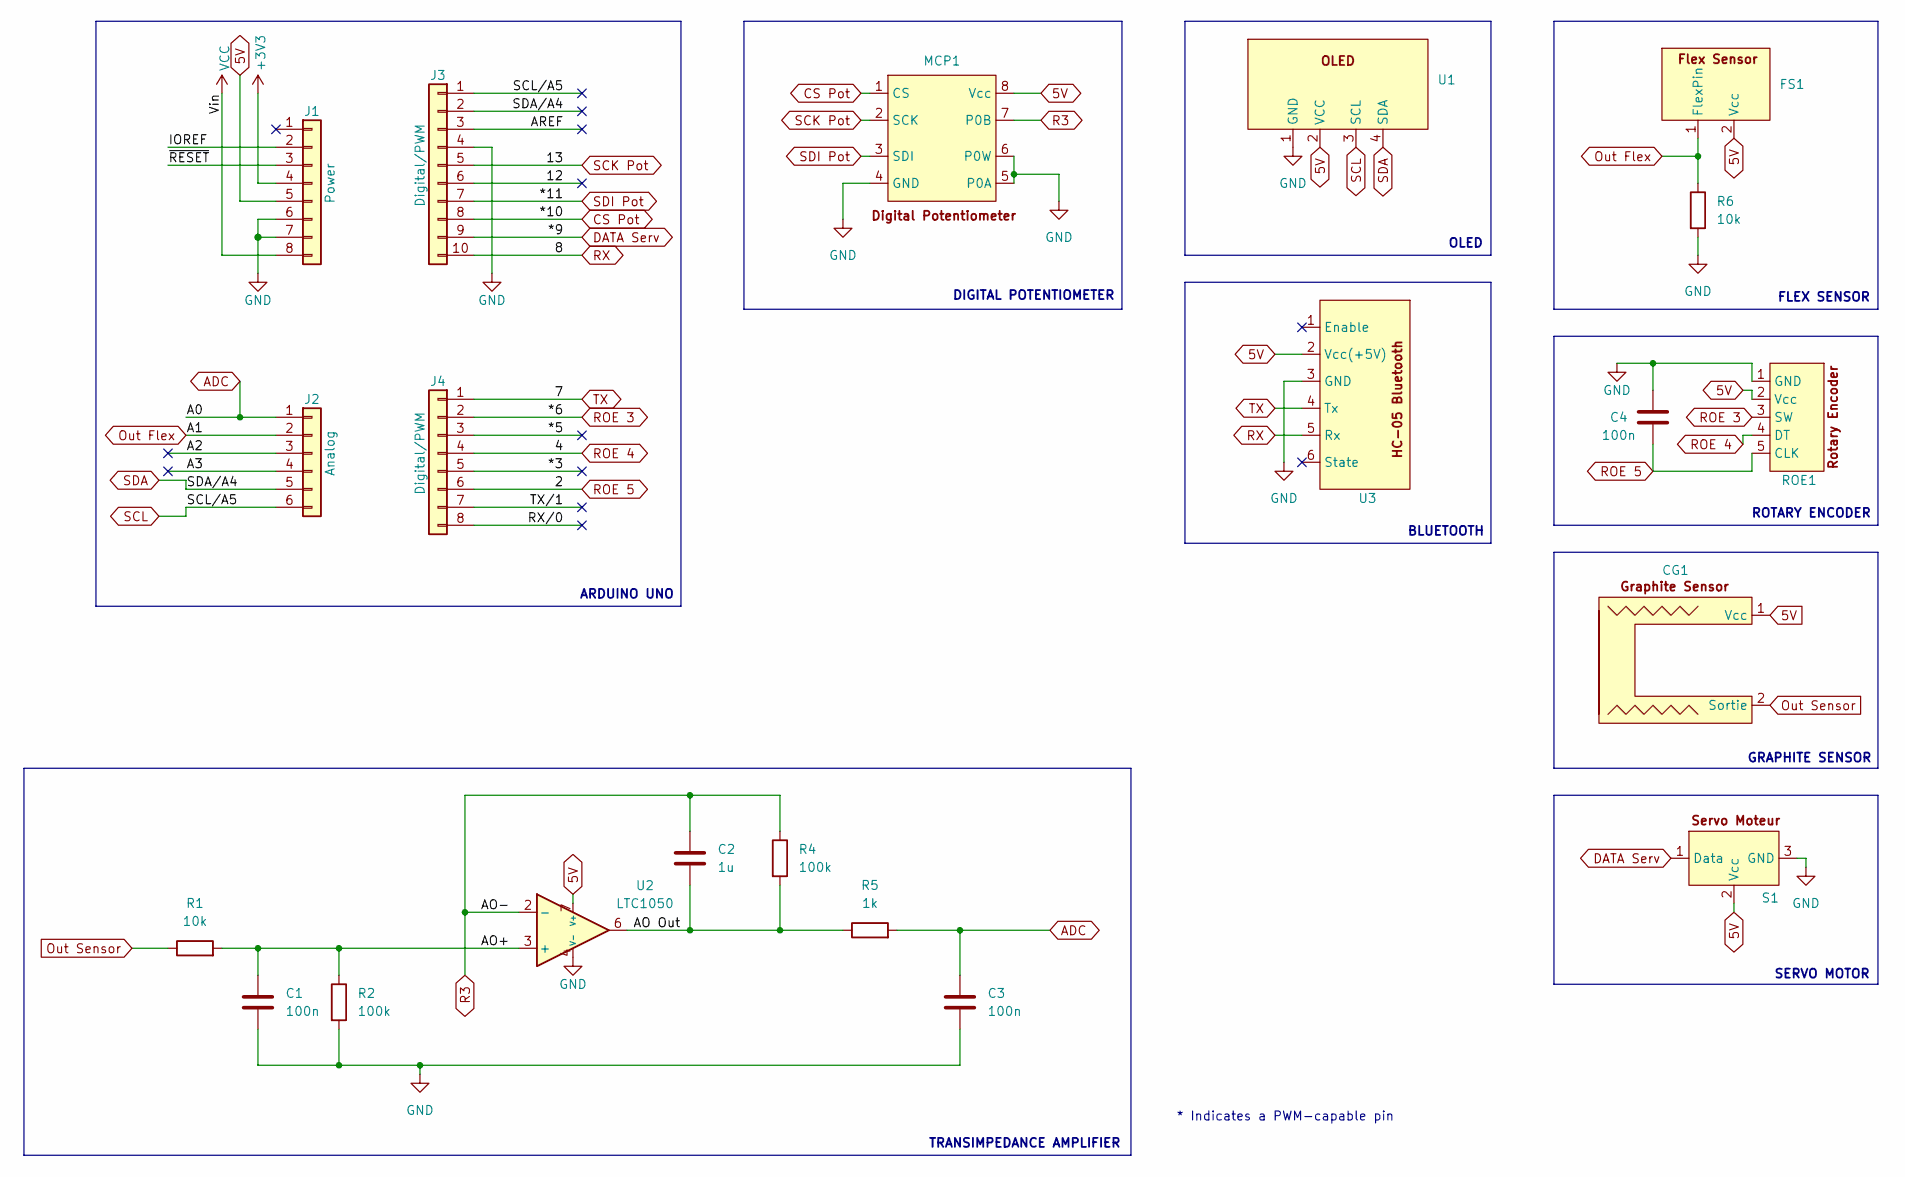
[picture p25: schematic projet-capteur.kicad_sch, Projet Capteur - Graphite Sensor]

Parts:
C1, C3, C4: 100n; C_Disc_D6.0mm_W2.5mm_P5.00mm
C2: 1u; C_Disc_D6.0mm_W2.5mm_P5.00mm
CG1: Capteur Graphene
FS1: Flex Sensor
J1: Power; PinSocket_1x08_P2.54mm_Vertical
J2: Analog; PinSocket_1x06_P2.54mm_Vertical
J3: Digital/PWM; PinSocket_1x10_P2.54mm_Vertical
J4: Digital/PWM; PinSocket_1x08_P2.54mm_Vertical
MCP1: DIP-8_W7.62mm
R1, R6: 10k; R_Axial_DIN0207_L6.3mm_D2.5mm_P5.08mm_Vertical
R2, R4: 100k; R_Axial_DIN0207_L6.3mm_D2.5mm_P5.08mm_Vertical
R5: 1k; R_Axial_DIN0207_L6.3mm_D2.5mm_P5.08mm_Vertical
ROE1: RotaryEncoder
S1: ServoMoteur
U1: MyEmpreinte
U2: LTC1050; DIP-8_W7.62mm
U3: HC-05

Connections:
5V: CG1.1 (Vcc), FS1.2 (Vcc), J1.5, MCP1.8 (Vcc), ROE1.2 (Vcc), S1.2 (Vcc), U1.2 (VCC), U2.7 (V+), U3.2 (Vcc(+5V))
+3V3: J1.4
/12: J3.6
/*3: J4.5
/*5: J4.3
/A2: J2.3
/A3: J2.4
/AO Out: C2.2, R4.2, R5.1, U2.6
/AO+: C1.1, R1.2, R2.1, U2.3 (+)
/AREF: J3.3
/IOREF: J1.2
/RX/0: J4.8
/TX/1: J4.7
/~RESET: J1.3
ADC: C3.1, J2.1, R5.2
CS Pot: J3.8, MCP1.1 (CS)
DATA Serv: J3.9, S1.1 (Data)
GND: C1.2, C3.2, C4.1, J1.6, J1.7, J3.4, MCP1.4 (GND), MCP1.5 (P0A), MCP1.6 (P0W), R2.2, R6.2, ROE1.1 (GND), S1.3 (GND), U1.1 (GND), U2.4 (V-), U3.3 (GND)
Out Flex: FS1.1 (FlexPin), J2.2, R6.1
Out Sensor: CG1.2 (Sortie), R1.1
R3: C2.1, MCP1.7 (P0B), R4.1, U2.2 (-)
ROE 3: J4.2, ROE1.3 (SW)
ROE 4: J4.4, ROE1.4 (DT)
ROE 5: C4.2, J4.6, ROE1.5 (CLK)
RX: J3.10, U3.5 (Rx)
SCK Pot: J3.5, MCP1.2 (SCK)
SCL: J2.6, J3.1, U1.3 (SCL)
SDA: J2.5, J3.2, U1.4 (SDA)
SDI Pot: J3.7, MCP1.3 (SDI)
TX: J4.1, U3.4 (Tx)
VCC: J1.8

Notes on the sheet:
ROTARY ENCODER
GRAPHITE SENSOR
DIGITAL POTENTIOMETER
ARDUINO UNO
FLEX SENSOR
SERVO MOTOR
BLUETOOTH
* Indicates a PWM-capable pin
OLED
TRANSIMPEDANCE AMPLIFIER

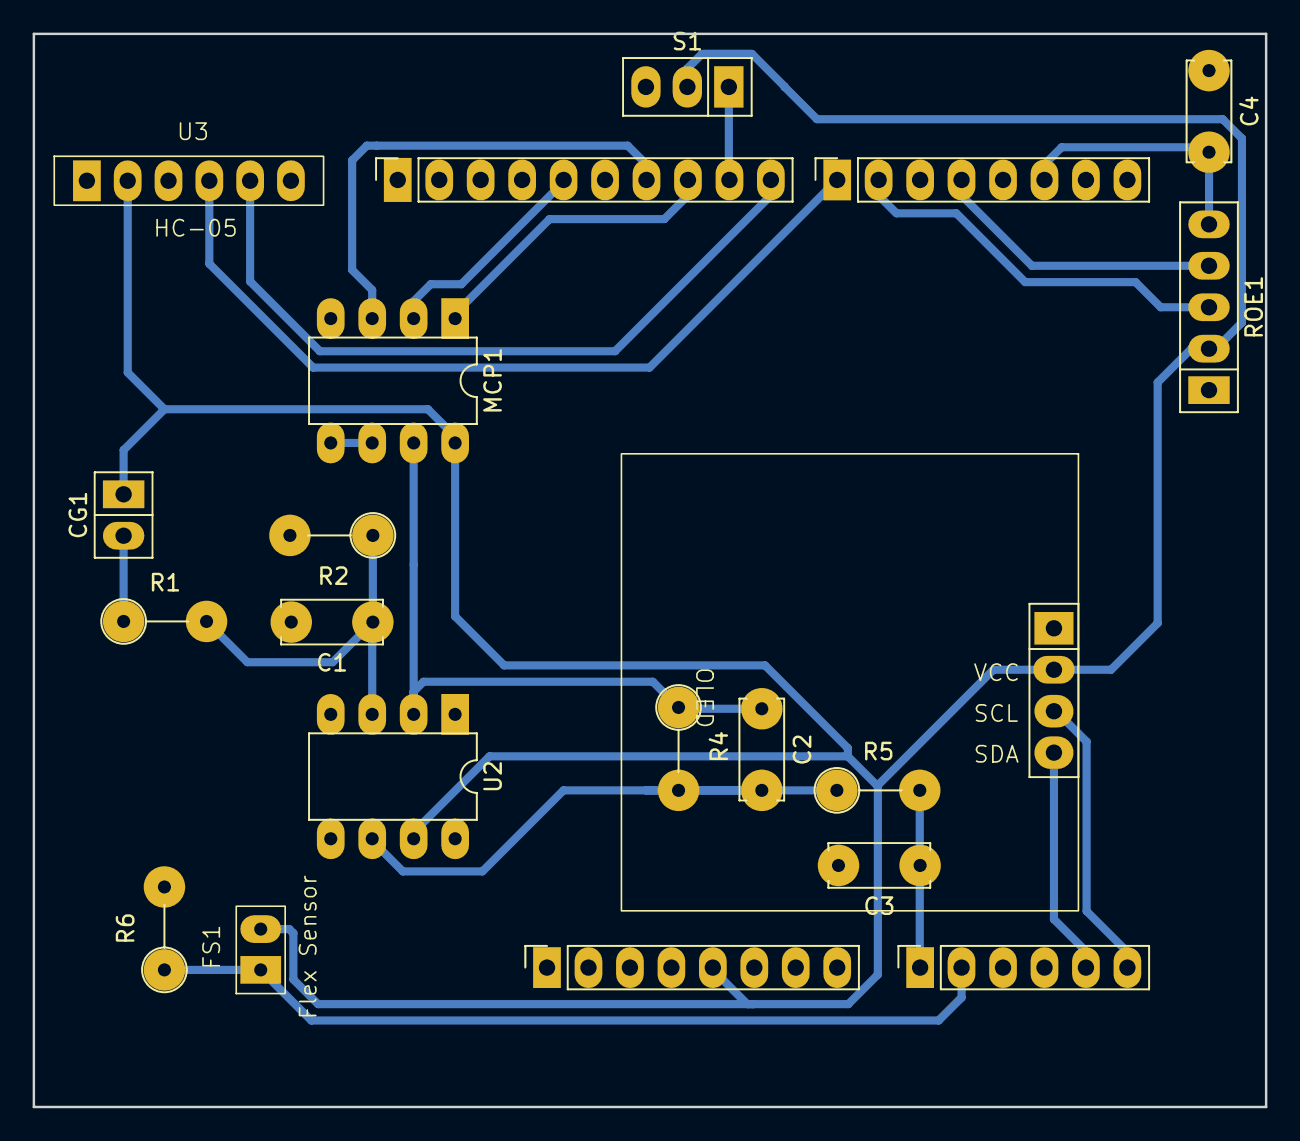
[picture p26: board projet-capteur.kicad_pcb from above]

Board: 2 copper layers, 75.5 x 65.8 mm, 21 parts (0 on the bottom side), 19 nets.

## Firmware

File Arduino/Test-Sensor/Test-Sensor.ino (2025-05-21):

#include <Servo.h>                          // Librairie Servo Moteur
#include <SoftwareSerial.h>                 // Librairie Bluetooth
#include <Adafruit_SSD1306.h>               // Librairie OLED
#include <Wire.h>                           // Utilisation de l'OLED
#include <SPI.h>                            // Librairie Potentiometre 
#include <RunningAverage.h>
#include <stdlib.h>

/* 
*   CONSTANTES ET DECLARATIONS : OLED
*/

#define nombreDePixelsEnLargeur 128         // Taille de l'écran OLED, en pixel, au niveau de sa largeur
#define nombreDePixelsEnHauteur 64          // Taille de l'écran OLED, en pixel, au niveau de sa hauteur
#define brocheResetOLED         -1          // Reset de l'OLED partagé avec l'Arduino (d'où la valeur à -1, et non un numéro de pin)
#define adresseI2CecranOLED     0x3C 

Adafruit_SSD1306 ecranOLED(nombreDePixelsEnLargeur, nombreDePixelsEnHauteur, &Wire, brocheResetOLED);

/*
*   CONSTANTES ET DECLARATIONS : BLUETOOTH
*/

#define RX_PIN                  7
#define TX_PIN                  8

SoftwareSerial mySerial(RX_PIN, TX_PIN);

/*
*   CONSTANTES ET DECLARATIONS : POTENTIOMETRE DIGITAL
*/

#define MCP_NOP                 0b00000000
#define MCP_WRITE               0b00010001
#define MCP_SHTDWN              0b00100001
#define ssMCPin                 10
int buffer1[512];
const int csPin                = 10;
const int maxPositions         = 256;
const long rAB                 = 33800;
const byte rWiper              = 125;
const byte pot0                = 0x11;
const byte pot0shutdown        = 0x21;
float R3;
float intposServo =0 ;
/*
*   CONSTANTES ET DECLARATIONS : ENCODEUR ROTATOIRE
*/

#define encoder0PinA            2  // CLK Output A Do not use other pin for clock as we are using interrupt
#define encoder0PinB            4  // DT Output B
#define Switch                  6  // Switch connection if available

volatile int encoder0Pos = 0;
int oldPOSencodeur = 0, buttonState = 0;

/*
*   CONSTANTES ET DECLARATIONS : SERVO MOTEUR
*/

#define servoPin                9

Servo myServo;

int posmoteur = 0;

/*
*   CONSTANTES ET DECLARATIONS : FLEX SENSOR
*/

#define flexPin                 A1

/*
*   CONSTANTES ET DECLARATIONS : GRAPHITE SENSOR
*/

#define graphitePin             A0
volatile int encoderFullPos = 0;
unsigned long previousMillis = 0;         // Important to check the time that has passed since the last millis()
float moy = 0;                            // Initialize mean to 0 in order to computate the average
char chaine[10],                          // Placeholder char variable of size 10 to display on the OLED
  cringe[16],  
  gain[10],
  posServo[10];                           // Placeholder char variable of size 16 to display on the OLED (to accommodate the larger values of the graphite resistance) i.e. I was annoyed when I found the solution. The name of the variable is fitting...
int inMenu = 0,                           // Value to see if the user has selected the menu
  Calibrated = 0;                         // Value to check if Calibration() has been completed

// #define WAIT_DELAY              5000

#define etat                    5
#define bufferSize              16
#define baudRate                9600

char bufferInput[bufferSize], constant = '0';

byte c = 0, Cgain = 0;                    // Quand on appelle un Serial.println(c), il faut que c ait une valeur. Sinon, ca va faire buguer l'OLED 


RunningAverage myRA(20);

void setup() {
  myRA.clear();

  pinMode (ssMCPin, OUTPUT);              // Select Pin Output
  digitalWrite(ssMCPin, HIGH);            // SPI Chip Disabled
  SPI.begin();
  
  if(!ecranOLED.begin(SSD1306_SWITCHCAPVCC, adresseI2CecranOLED))
    while(1);     

  ecranOLED.clearDisplay();

  pinMode(encoder0PinA, INPUT); 
  digitalWrite(encoder0PinA, HIGH);       // Turn on Pullup Resistor

  pinMode(encoder0PinB, INPUT); 
  digitalWrite(encoder0PinB, HIGH);       // Turn on Pullup Resistor

  pinMode(Switch, INPUT);
  digitalWrite(Switch, HIGH);             // Turn on Pullup Resistor

  attachInterrupt(0, doEncoder, RISING);
  pinMode(flexPin, INPUT); 

  Serial.begin(baudRate);
  mySerial.begin(baudRate);

  myServo.attach(servoPin);
  
  delay(1000);

  Serial.println(F("[Arduino Sensor - HAHN & LONGEPIERRE]"));

  Calibration();  
  clearRead();                     // Oublie pas a enlever le commentaire
}

/*
*   Dsiplays the menu on the OLED screen
*/

void loop() {
  menuChoice();
  if (mySerial.available() > 0) {
    c = mySerial.read();
    c = c + 0;
    
    if (c == 'f')
      if (mySerial.read() == 'f')
        if (mySerial.read() == 'f')
          if (mySerial.read() == 'f') {
            encoder0Pos = 1;
            inMenu = 1;
          }
    if (c == 'g')
      if (mySerial.read() == 'g')
        if (mySerial.read() == 'g')
          if (mySerial.read() == 'g') {
            encoder0Pos = 0; 
            inMenu = 1;
          }
    if (c == 's')
      if (mySerial.read() == 's')
        if (mySerial.read() == 's')
          if (mySerial.read() == 's') {
            encoder0Pos=2;
            inMenu=1;
          }
    if (c == 'c')
      if (mySerial.read() == 'c')
        if (mySerial.read() == 'c')
          if (mySerial.read() == 'c') {
            Calibrated = 0;
            Calibration();
          }
    clearRead();
  }
}

/*
*   Reads if switch button on the rotary encoder has been pushed
*/

void getSW() {

  if (!(digitalRead(Switch))) {
    if (inMenu == 0)
      inMenu++;
    else
      inMenu--;
  }
}

/*
*   Sets the position of the Digital Potentiometer
*/


void setPotWiper(int addr, int pos) {
  pos = constrain(pos, 0, 255);
  digitalWrite(csPin, LOW);
  SPI.transfer(addr);
  SPI.transfer(pos);
  digitalWrite(csPin, HIGH);

  R3 = ((rAB * pos) / maxPositions) + rWiper;
}

/*
*   Calibrates the received signal at 3V with a tolerance of 0.15V
*/

void Calibration() {
  float target = 2.5, tol = 0.4;
  int pos = 0;

  do {
    setPotWiper(pot0, pos);
    pos += 2;
    delay(100);
  } while ((graphiteSensor() < (target - tol) || graphiteSensor() > (target + tol)) && pos <= 265);
  
  dtostrf(pos, 5, 2, chaine);
  
  if (pos < 265) {
    Serial.println(F("Potentiometer calibrated at position : "));
    Serial.print(chaine);

    float val = graphiteSensor();
    dtostrf(val, 10, 2, chaine);
    dtostrf(pos, 5, 0, gain);
    Cgain=pos;
    setPotWiper(pot0, Cgain);
    Serial.println(F("Value : "));
    Serial.print(chaine);
  }
  else {
    Serial.println(F("Potentiometer not calibrated at target 3V"));
    setPotWiper(pot0, Cgain);
  }
  Calibrated = 1;
} 

/*
*   Reads the rotary encoder's rotation (clockwise or counter-clockwise)
*/

void doEncoder() {
  if (inMenu == 0) {
    if (digitalRead(encoder0PinA)==HIGH && digitalRead(encoder0PinB)==HIGH) {
      encoder0Pos++;
    } 
    else if (digitalRead(encoder0PinA)==HIGH && digitalRead(encoder0PinB)==LOW) {
      encoder0Pos--;   
    }
    encoder0Pos %= 3;
  }
  if (digitalRead(encoder0PinA)==HIGH && digitalRead(encoder0PinB)==HIGH) {
     encoderFullPos+=18;
   } 
   else if (digitalRead(encoder0PinA)==HIGH && digitalRead(encoder0PinB)==LOW) {
     encoderFullPos-=18;   
   }
   encoderFullPos = (encoderFullPos) %180;
  //Serial.println (encoder0PinA, DEC);  //Angle = (360 / Encoder_Resolution) * encoder0Pos
}

/*
*   Clears the bluetooth's buffer
*/

void clearRead() {
  while (mySerial.available() > 0) {
    byte a = mySerial.read();
  }
}

float flexSensor() {
  float ADCflex = analogRead(flexPin);
  int VCC = 5; // 5V
  int R_DIV = 10000;
  float Vflex = ADCflex * VCC / 1024.0;
  float Rflex = R_DIV * (VCC / Vflex - 1.0);
  byte toBlue = ADCflex / 4.0;

  mySerial.write(toBlue);

  return Rflex;
}

/*
*   Retrieves the Graphite Sensor's value 
*/

float graphiteSensor() {
  float R2 = 100000, R1 = 10000, R4 = 100000, Res;
  float ADCgraph = analogRead(graphitePin);
  int VCC = 5;
  float Vgraph = ADCgraph * VCC / 1024.0;
  
  Res = R2 * (1 + R4/R3) * (VCC / Vgraph) - R2 - R1;
  mySerial.write(ADCgraph / 4);

  if (Calibrated == 0) {
    return Vgraph;
  }
  else {
    return Res;
  }
}

/*
*   Sends the value to the Servo Motor
*/

int servoMotor() {
  int val = 0;
  static int xd = 0;
  char str[256];
  int i = 0, bytes;

  return val;
}

/*    
*     Menu Choice :
*     1 : Graphite Sensor
*     2 : Flex Sensor
*     3 : Servo Motor
*/
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

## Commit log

2025-03-05 Ajout des fichiers de bases
    [DIP-8 W7.62mm IC with Socket.stp, HC05.STEP, OLED 0.96_ V2.0 v1.step, rotary+encoder_14mm_hole_spc.stp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]
2025-03-08 Remis les empreintes perdues
    [DIP-8 W7.62mm IC with Socket.stp, HC05.STEP, OLED 0.96_ V2.0 v1.step, projet-capteur.kicad_pcb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]
2025-03-08 Ajout ecran OLED + Schema
    [OLED 0.96_ V2.0 v1.step, projet-capteur.kicad_pcb, projet-capteur.kicad_sch]
2025-03-08 Ajout du HC-05
    [projet-capteur.kicad_pcb, projet-capteur.kicad_sch]
2025-03-08 rajout des condesateur sur le pcb
    [projet-capteur.kicad_pcb, projet-capteur.kicad_sch]
2025-03-08 pin a jour pour le ltc1050 hc05 connecté
    [projet-capteur.kicad_pcb, projet-capteur.kicad_sch]
2025-03-10 Ajout du Flex Sensor et DPotentiometre
    [FS-L-0095-103-ST - Assembly.stp, projet-capteur.kicad_pcb, projet-capteur.kicad_sch]
2025-03-12 Ajout du header Servo Moteur
    [projet-capteur.kicad_pcb, projet-capteur.kicad_sch]
2025-03-12 Seance Realisation du shield 12.03
    [projet-capteur.kicad_pcb, projet-capteur.kicad_sch]
2025-03-12 Seance Realisation du shield 12.03 v2
    [projet-capteur.kicad_pcb, projet-capteur.kicad_sch]
2025-03-12 Ajout dossier Gerber
    [projet-capteur.kicad_pcb]
2025-03-12 Changement des positions du encodeur
    [projet-capteur.kicad_pcb]
2025-03-13 Seance Realisation du shield 13.03
    [projet-capteur.kicad_pcb, projet-capteur.kicad_sch]
2025-03-16 Modif des tracks + pins
    [projet-capteur.kicad_pcb, projet-capteur.kicad_sch]
2025-03-16 Reparation des pins du potentiometre
    [projet-capteur.kicad_pcb, projet-capteur.kicad_sch]
2025-03-17 Correction du Bluetooth
    [projet-capteur.kicad_pcb, projet-capteur.kicad_sch]
2025-03-17 Seance Realisation banc de test 17.03
    [projet-capteur.kicad_pcb, projet-capteur.kicad_sch]
2025-03-17 Grandissement du shield
    [projet-capteur.kicad_pcb, projet-capteur.kicad_sch]
2025-03-18 Modif Rot
    [projet-capteur.kicad_pcb]
2025-03-18 Beautification du PCB
    [projet-capteur.kicad_pcb, projet-capteur.kicad_sch]
2025-03-28 Ajout du dossier Arduino
2025-03-31 Amelioration de la Datasheet
2025-04-07 Arduino - Menu presque fini
2025-04-07 README - Modif et Arduino - Menu 3
2025-04-08 Arduino - Modif du 08.04
2025-04-08 Beautification du Schematique
    [projet-capteur.kicad_pcb, projet-capteur.kicad_sch]
2025-04-10 README - Ajout des photos simu
2025-04-11 Test Bench
    [Test-Bench.xlsx]
2025-04-14 Datasheet - Correction typos et Arduino - Fonction Calibration
2025-04-15 Arduino - Click Switch
2025-04-17 Arduino - Comments added
2025-04-24 Arduino - Fonction recevoir BT
2025-04-26 Reception bleutooth mise en place + controle app to arduino
2025-04-27 Arduino - Comments + Correction et ReadME - Android et Arduino
2025-04-29 Update Test-Sensor.ino version final coté axel
2025-04-29 Arduino - Improved readability
2025-05-21 Update Final Test-Sensor.ino
    FINITOT pipo
2025-05-24 Final Version
    [Test-Bench.xlsx]
